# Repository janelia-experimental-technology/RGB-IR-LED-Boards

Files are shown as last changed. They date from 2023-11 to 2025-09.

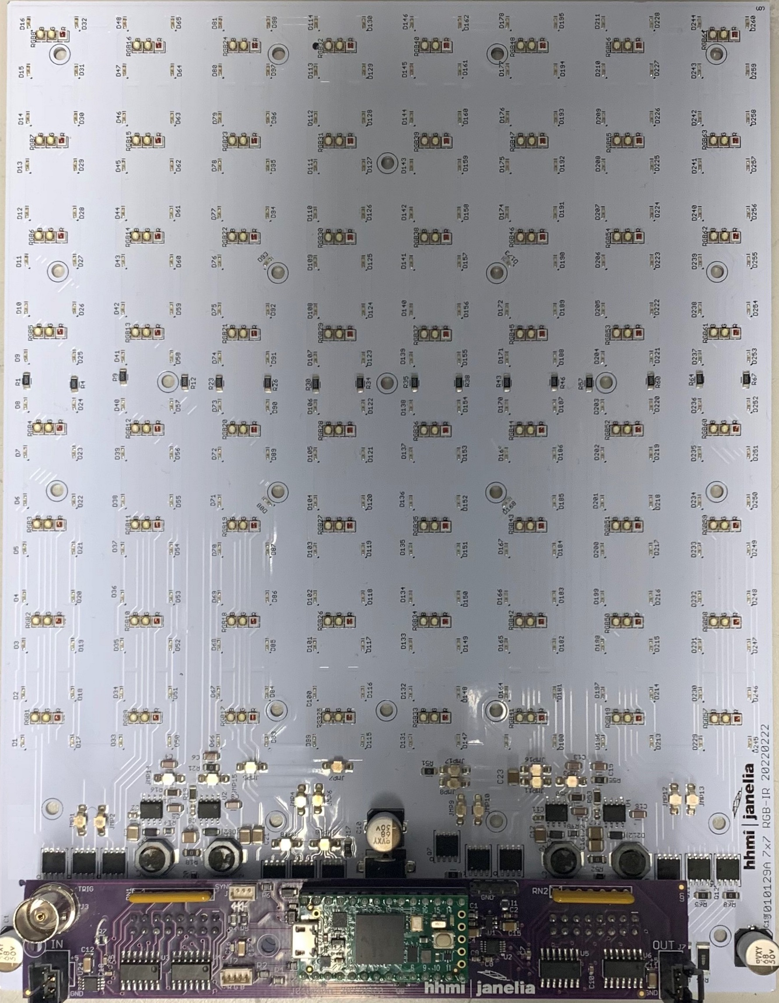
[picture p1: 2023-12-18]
RGB-IR Backlight 7x7/7x7RGB.jpg

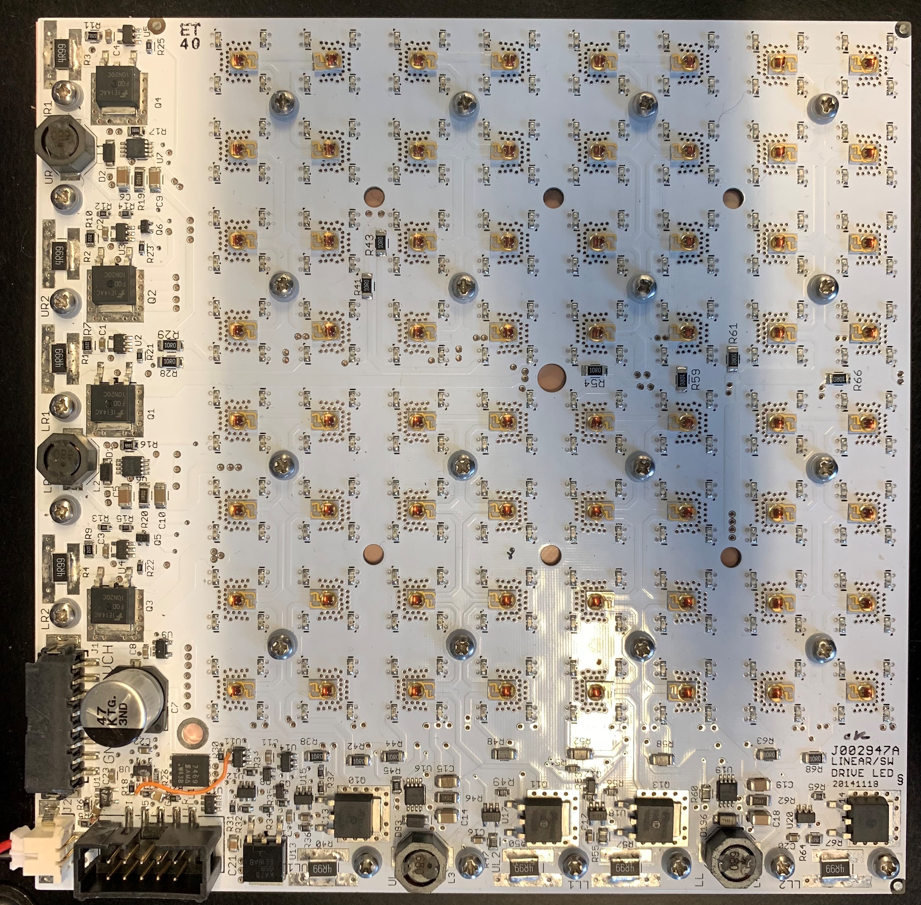
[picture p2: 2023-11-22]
RGB-IR Backlight SingleColor/Electrical/LEDboard-J002947A/J002947A.jpg

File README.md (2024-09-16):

# RGB-IR-LED-Boards
 RGB-IR backlights 
Various LED boards that provide color and IR lighting (primarily for backlighting) in steady or pulsed modes. 
The boards are controlled by a USB-Serial command interface that provides a wide variety of opearting modes.
The 5x5 single color and RGB Combined Color have been depracated and are for reference only. 
The cuurent boards have LED areas of 5" x 5" or 7" x 7" and use separate LEDs for each color, allowing up to
three colors to be used on one board (in addition to IR). The firmware and command interace is common to all 
boards, though some features may not be available on all boards.

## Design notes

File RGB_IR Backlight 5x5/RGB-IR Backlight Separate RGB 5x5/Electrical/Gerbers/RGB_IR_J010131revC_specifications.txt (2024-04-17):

RGB_IR_J010131revC_specifications

2 layers 
0.8mm finished thickness
2 oz copper
white soldermask with black silkscreen

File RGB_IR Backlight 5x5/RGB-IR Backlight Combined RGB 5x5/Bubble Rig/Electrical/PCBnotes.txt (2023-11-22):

The RGB-IR board should be 0.032" thickness with 2 oz copper traces

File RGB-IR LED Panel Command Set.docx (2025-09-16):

RGB-IR LED Panel Command Set

Steve Sawtelle
Lead Electrical Engineer, ID&F
(571) 209-4158

# System Overview

The command set for the RGB-IR LED panels is common to all versions of the 5” x 5” and 7”
x 7” panels designed at Janelia Research Campus of HHMI.

# Firmware Development

The firmware is written in Arduino with Teensyduino extensions. Several libraries are used:

Cmd.h – This has been modified from the version available on Github to add features needed by the firmware. It processes commands sent over USB-Serial and is used to set up parameters and create actions.

Watchdog.h – This is a library written by Peter Polidoro to set up and control a watchdog timer in case the firmware hangs up.

EEPROM.h – This library is used to save setups in non-volatile memory, such as offsets and gains for each quadrant to make the quadrants light intensity more even (especially at low levels).

Several Teensy varieties are supported. The preferred boards are the Teensy 3.2 and 4.0. The LC can be used but has limited memory for Experiment Command Steps. The firmware will compile correctly based on the chosen processor.

The RGB firmware is command driven. The processing of commands is handled by the cmd.h library, which will call the appropriate function once the command line is parsed. These functions end in ‘cmd’. The commands can set up parameters, query settings, or cause action. Commands are ASCII and case insensitive. Parameters are separated by spaces or commas. The command is terminated with a linefeed and carriage return.

Pulse timing or a loaded experiment is based off a millisecond clock, so the basic accuracy of the board is one millisecond. The processing of pulse timing or a loaded experiment is controlled via a four-phase state machine. Each phase runs independently and is associated with one of the three color channels or digital channel. For each phase, an initial state is called, which sets up parameters and timing for the next state. A flag is set to note a change in state and the next state will wait until the last state has completed before it executes its function and sets up the next state.

# There are several compiler defines that affect the operation of the firmware:

# DEBUG – turns on debugging information on USB-serial output.

SYNC_PIN_OUT – if defined, the SYNC pin is set up as output, otherwise it set up as trigger input.

SYNC_ACTIVE_LOW – if defined, the SYNC pin is active low.

# Command Set

The host communications is via a USB-serial link. The Teensy serial driver must be loaded on the host (available from PJRC.com). The link is baud-independent. The communications protocol is based on an ASCII commands with various parameters. Commands are not case sensitive and must be terminated with a carriage return character (‘\r’, 0x0D). Basic error checking is done and ‘cmderr n’ is returned with ‘n’ being a negative integer that can be used to determine the type of error. Commands may return other information to the Host to indicate status. These are still under development.

NOTE: the 7” x 7” RGB panels do not have addressable ‘Quadrants’. For these boards, the ‘Quadrant’ value should be left blank or set to ‘1111’ to select all quadrants.

The following commands are supported:

RESET – reset all boards to their power-on state. This should always be sent at the beginning of a session or after power has been cycled.

RED b p q (or) - control for red (chrimson) LEDs

CHR b p q

BLUE b p q (or) – control for blue LEDs

BLU b p q

GREEN b p q (or) – control for green LEDs

GRN b p q

IR b p q – control for infrared LEDs

Where:

‘b’ is the brightness as a percentage (0-100). A floating-point value can be used.

‘p’ (optional) is the panel to be changed. No value (or 0) will change all panels. 1-4 will select that panel

‘q’ = quadrant(s): 0 = all, or bit pattern (“0011” means turn on quadrants 1 and 2)

These commands control the LED intensity for red, blue, green, or infrared, respectively. For RGB LEDs, very low values (<1%) may show different intensities across the LEDs since they are close to their turn-off state. The RGB LEDs use linear drivers, so the intensity is very linear down to low levels. Note that for RGB LEDs this command only sets intensity, it does not turn the LED on. Use ON and OFF to control LED state. For IR LEDs, the settings should be above 15% due to the way the driver for these LEDs works. To turn off IR, set the intensity to 0%, as IR LEDs do not have separate ON or OFF commands.

Note: If low, equal, intensities are needed, the maximum current can be modified with a hardware change (see Hardware Technical Document for the board), or the offset value for each quadrant can be adjusted by the Offset command.

Note: the current board design uses separate LEDs for each color, enabling one to choose any mix of available colors. If colors other than red, green, or blue are used, then on will need to keep track of which custom color is associated with each channel name.

ON p q – turn on RGB LEDs to their last setting, optional panel(s) and quadrant(s)

OFF p q – turn off RGB LEDs, optional panel(s) and quadrant(s)

When the RGB LEDs are set to an intensity, that value is stored. Use ON and OFF to turn RGB LEDs on and off.

‘p’ = panel(s): 0 = all, or 1, 2, 3, or 4 for an individual panel

‘q’ = quadrant(s): 0 = all, or bit pattern (“0011” means turn on quadrants 1 and 2)

PULSE width, period, number, off, wait, iterations, color - pulse setup command

The PULSE command sets up a pulse train to light Optogenetic LEDs that have been set up with an ON or PATT command. The pulse has: on delay, pulse width, period, number of cycles, off delay, wait time, and number of iterations. WAIT

width: The pulse width (on time) in milliseconds from 1 to 30000

period: The period of the pulse (on time plus off time) in milliseconds from 1 to 30000. If the width and period are equal, then the LEDs are on constantly during the pulse train.

number: The number of pulses in a pulse train. One pulse train starts with an on time and ends ‘number’ of pulse later after the last off time.

off: The off time after the pulse train completes in milliseconds from 0 to 30000. This provides a means to have a dead time between pulse trains if iterations are used. Note that the total off time from when the last pulse on time ends to the next pulse on time starts is equal to: off + period – width.

wait: Delay the start of the pulse sequence in seconds from 0 to 120. This delays the start of the very first pulse after the RUN command is sent. It is not repeated until RUN is resent. A floating-point value can be used here to set timing to the millisecond level.

iterations: The number of time the pulse train is repeated from 0 to 30000. A ‘0’ value runs the pulse train continuously until a STOP command is sent.

color: Which color the pulse command is for (‘R’, ‘G’, and/or ‘B’) – the three characters can be used in any combination. If different pulse setups are required for different colors, then use separate PULSE commands.

The diagram below shows how each parameter fits into the pulse train:

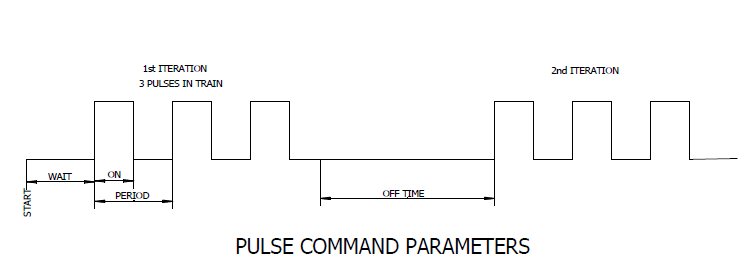
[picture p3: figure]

RUN c- Start running the pulse sequence, optional color(s)

- c – color(s) any combination of ‘R’, ‘G’, ‘B’

STOP c- Stop running the pulse sequence and reset to the beginning, optional color(s)

- c – color(s) any combination of ‘R’, ‘G’, ‘B’

PAUSE – Pause the current pulse sequence

MARKER c s – turn a marker LED on or off.

- c – color: ‘R’, ‘G’, ‘B’, ‘D’
- s – state “ON” or “OFF”

BLINK t c – turn the marker LEDs on for ‘t’ milliseconds. This pattern will also be repeated at the beginning of Each experiment Step.

- c – color(s) any combination of ‘R’, ‘G’, ‘B’

DIGITAL p – set up digital outputs according to bit pattern ‘p’

DON – turn on digital outputs that were enabled with the DIGITAL command

DOFF – turn off digital outputs

SYNC f – send sync pulses out Sync connector at frequency ‘f’ (floating point). If ‘f’ = 0, then turn of sync output. If ‘f’ is blank, return current sync rate.

SYNCON – start sync signal at previously specified rate

??? - Returns the version number and other parameters

HELP - Returns a list of the available commands

EXPERIMENT COMMANDS

A complete experiment can be downloaded to the board, consisting of individual steps that run one after the other. Steps can be loaded in any order, with ‘1’ being the first step. An experiment will stop at the end of the steps (or the first missing step).

addOneStep(parameters): upload one experiment step to the buffer with the following parameters:

StepNumber,

RedIntensity, RedPulsePeriod, RedPulseWidth, RedPulseNum, RedOffTime, RedIteration,

GrnIntensity, GrnPulsePeriod, GrnPulseWidth, GrnPulseNum, GrnOffTime, GrnIteration,

BluIntensity, BluPulsePeriod, BluPulseWidth, BluPulseNum, BluOffTime, BluIteration,

DelayTime, Duration(step), [optional] pattern )

Where:

The Intensity, Period, Width, Number, Off Time, Iteration are the same as the PULSE command

Delay Time is the same as the PULSE command but is common for all three colors

Duration is the total duration of the step

Pattern is the quadrant pattern use (16 bits)

getExperimentsteps (or GS): returns a list of entered steps

removeAllSteps: remove all steps

runExperiment (or RX): run the entered experiment

stopExperiment (or SX) : stop the experiment in progress

getExperimentStatus (or GX): returns the current step being processed during a run

stepOrder n: add a series of numbers, one at a time, designating the sequence the entered Experiment Steps should be run in (if not used, the experiment is run in the step sequence, one time). For example, if 2 steps are entered, sending:

steporder 2

steporder 1

steporder 1

steporder 2

will run step 2, then step 1, then step 1 again, then step 2 when the runExperiment command is sent.

Sending stepOrder 0 will reset the steps, sending stepOrder with no parameter will list the step order.

CALIBRATION COMMANDS

The RGB_IR board should have uniform light output. However, the 5x5 board, with separate quadrant control, may show some differences at low light levels. If an experiment requires background subtraction, then the brightness of each quadrant can be adjusted so that, at a given IR setting, the backlight is more uniform. The light levels can be calibrated using the OFFSET and GAIN commands. These values are stored in non-volatile memory and will be loaded at power up. The offset values represent digital-to-analog converter (DAC) counts. The DAC can range from 0 to 4095. The brightness is calculated as follows:

output value = set value * GAIN + OFFSET

Gain

The GAIN command was added to enter in gain values. These values default to 1.0 and can range from 0.8 and 1.2, but generally, gain changes of 5% or less are enough. A new board has the gains all set to 1.0. There are sixteen gain values: one for each quadrant and for each color. The IR gain is probably the most important as it sets the continuous backlight that is used for automatic tracking. The color LEDs are normally used for optogenetics, and small differences are not as critical.

GAIN c, q, g – set the gain value for a quadrant

Where:

‘c’ is color to be adjusted (‘R’, ‘B’, ‘G’, or ‘I’).

‘q’ = quadrant(s): 0, 1, 2, or 3

‘g’ is the gain multiplier (0.8 to 1.2)

If the GAIN command is sent without parameters, the current settings are returned:

GAIN

BLU 1.00 1.00 1.00 1.00

GRN 1.00 1.00 1.00 1.00

RED 1.00 1.00 1.00 1.00

IR 1.00 1.00 1.00 1.00

To change the gain of a quadrant, the GAIN command has parameters of Color, Quadrant, and Gain:

GAIN BLUE 0 1.1

The color can be spelled out or a shortened version can be used (RED, GRN, BLU, IR) or, simply, just the first letter is needed (R,G,B,I). The commands are case insensitive.

The Quadrant is a value between 0 and 3 inclusive, starting with the quadrant closest to where the cables attach, and increasing clockwise:

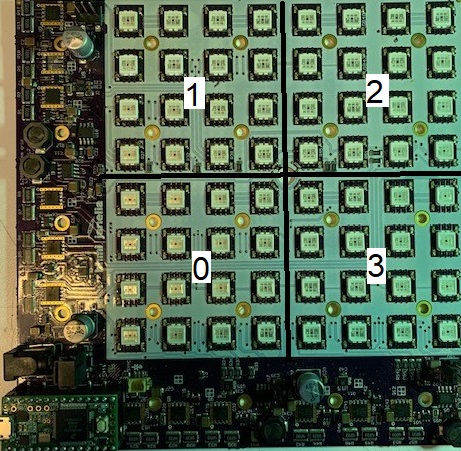
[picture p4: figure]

An example is the Fly Bubble Rig, where the quadrants can be counted relative to the hole at one corner:

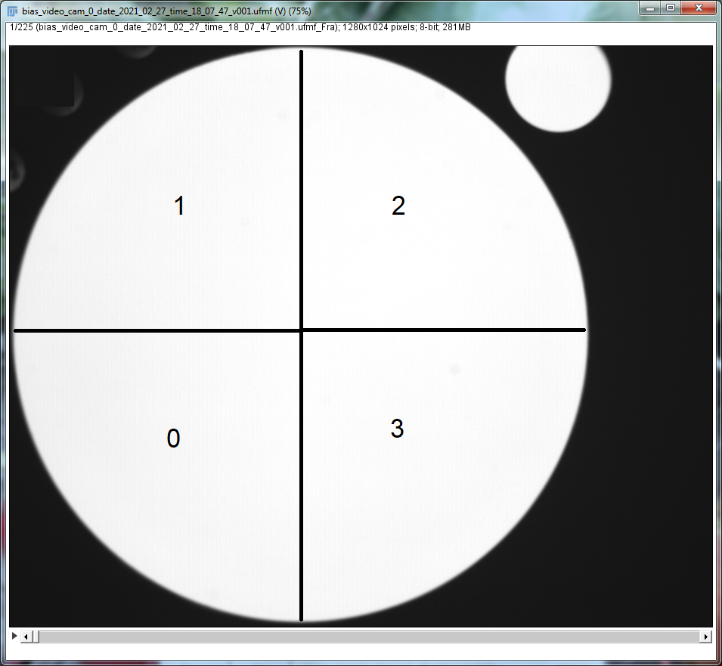
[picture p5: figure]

The Gain is a floating-point value between 0.8 and 1.2 inclusive. Lower gain reduces the relative brightness of the selected quadrant.

An Intensity Command for the chosen color and quadrant must be sent to see the effect of a gain change. So, if IR is changed for quadrant 1, then sending:

IR 30

Will update all the IR’s with appropriate gains.

Choosing the correct gains is somewhat interactive. The easiest method is to set the chosen color to a set intensity for all quadrants slightly below the saturation level, for example:

IR 40

Log a video or single frame of the board using BIAS or other camera software. Open that file in FIJI or other analysis software. Look at profiles of adjacent quadrants:

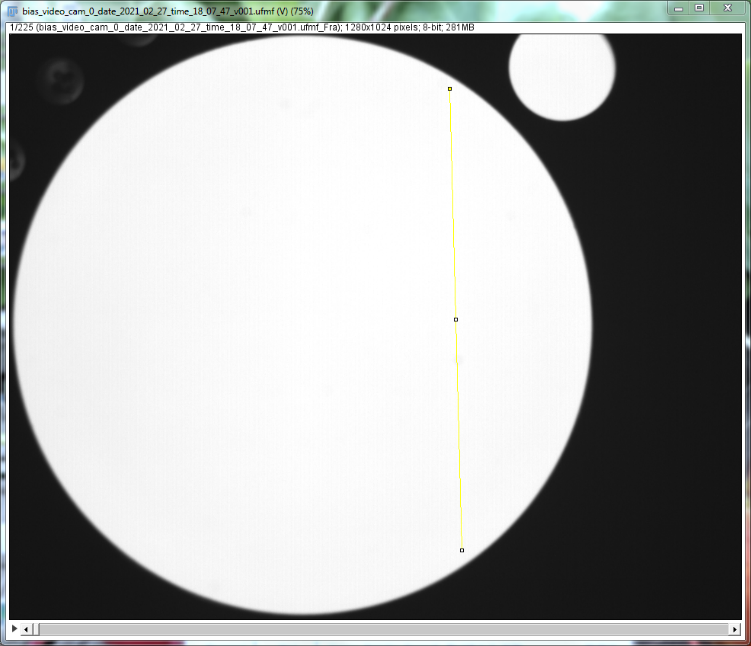
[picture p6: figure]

Here a profile line was drawn through the quadrants 2 and 3. Do this to the other three combinations. It will be clear which quadrants are different than the others. If one quadrant is higher intensity, it’s gain can be lowered, or if one quadrant is lower, it’s gain can be increased. 5% changes are usually enough. Change the IR level to make the gain take effect and repeat until the profiles are sufficiently uniform.

Once the profiles are uniform, the gain changes are complete. The GAIN command, without parameters, can be used to list the changes made. These changes are stored in non-volatile memory, so they are reinstated after a power cycle or reset. However, if the device is reprogrammed with updated firmware, the values may be lost. It would be wise to make note of the values once changes are finalized.

Offset

A zero offset can be applied to each quadrant in a similar way to gain. This is primarily used to get more even brightness at very low settings (less than 2%). Offset values can range between 0 and 20 and is in units of digital-to-analog converter (DAC) counts. The DAC has a range of 0 to 4095 counts.

OFFSET c, q, o – set the offset value for a quadrant.

Where:

‘c’ is color to be adjusted (‘R’, ‘B’, ‘G’, or ‘I’).

‘q’ = quadrant(s): 0, 1, 2 or 3

‘o’ is the offset value (0 to 20)

If no parameters are specified, then the current settings are returned.

# Intraboard Commands

This section describes the commands sent between boards. These commands are not directly available to the host but are included here to provide detail on how host commands are relayed to the other panels. The intraboard communications is based on a TTL serial link using the Teensy Serial1 port. Each panel has an input and output line. All boards have a Teensy installed, but only one (main panel) is connected to the host. The host sends all commands to all or any other panel(s) via the main panel. The main panel interprets the command from the host, and if is destined for one or more other panels, it sends the command on via Serial1. The incoming serial connection to the panel is always connected to the micro’s Serial1 receive port and the outgoing serial connection leaving a panel is routed through a TX/RX switch to route signals. The panel’s output signal can be switched between a direct connection to the input (Parallel Mode) or connected to the panel’s Serial1 transmit port (Series Mode).

Initially, all panels boot up in Parallel Mode. On reset, the main panel will send a Series command to put the attached panels in daisy-chain mode. This is necessary so that the boards can enumerate so they know what position they are in. An initial Enumerate1 command by the main panel propagates to the second panel, which configure itself as panel 2, and it the sends out an Enumerate2 to the second panel. This panel then configures itself as panel 3, and sends an Enumerate3 command to the last panel. After allowing time for the commands to propagate, the main panel sends a Parallel command to set the panels back to normal operation. Then any commands from the main panel are passed directly to all panels simultaneously to minimize delay of commands between panels. Each command is a single 8-bit value. The 256 possible commands are organized as follows:

Commands

00pp bbbb Turn off selected quadrants on selected panels

pp = panel (00 = all, 01 = 1, 10 = 2, 11 = 3)

bbbb = quadrant bits quadrant bits (0b0001 is upper left, 0b0010 upper right, 0b1000 lower right, 0b0100 lower left

01pp bbbb Turn on selected quadrants on selected panels

pp = panel (00 = all, 01 = 1, 10 = 2, 11 = 3)

bbbb = quadrant bits quadrant bits (0b0001 is upper left, 0b0010 upper right, 0b1000 lower right, 0b0100 lower left

10pp qqcc Set intensity command of selected panel(s), quadrants(s) , and color(s) to last Intensity value (0-4095)

pp = panel (00 = all, 01 = 1, 10 = 2, 11 = 3)

qq = quadrant number 00 is upper left, etc.

cc = color (00 = BLU, 01 = RED, 10 = GRN, 11 = IR)

1100 iiii Set the lower 4 bits of the intensity value (or lowest 4 bits of digital pattern)

iiii = intensity value nibble

1101 iiii Set the middle 4 bits of the intensity value (or middle 4 bits of digital pattern)

iiii = intensity value nibble

1110 iiii Set the highest 4 bits of the intensity value (or highest 4 bits of digital pattern)

iiii = intensity value nibble

1111 00xx Enumerate

xx = 01 sent by main board, 10 sent by next panel, 11 sent by third panel

1111 0100 Set RX/TX switch to Series mode

1111 0101 Set RX/TX switch to Parallel mode

1111 1ddd Turn color DACs on or off on all panels (used for fast response, especially for pulsing

ddd = color DACs: bit 2 = red, bit 1 = green, bit 0 = blue

1111 0000 When in parallel mode, turns red marker off

1111 0000 When in parallel mode, turns green marker off

1111 0000 When in parallel mode, turns blue marker off

1111 0111 When in parallel mode, sets digital pin pattern from last pattern sent with Intensity command

1111 0001 When in parallel mode, turn digital outputs on

1111 0011 When in parallel mode, turn digital outputs off

1111 0101 When in parallel mode, turn digital marker off

IR-Optogenetic Panel Controller

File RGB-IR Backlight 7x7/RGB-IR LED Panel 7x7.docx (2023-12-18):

7” x 7” RGB-IR LED Panel

J0010129 and J010130

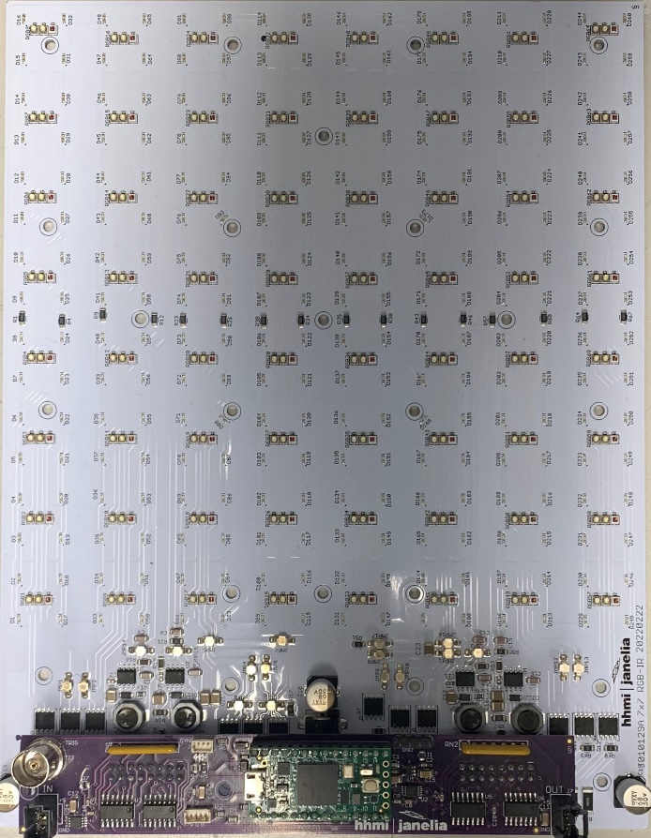
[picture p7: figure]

Steve Sawtelle
Electrical Engineer, ID&F
(571) 209-4000

# System Overview

The RGB-IR LED Panel is used to provide three colors and IR lighting of various intensities. The standard design uses red, green, and blue (RGB) LEDs, but since separate LEDs are used for each color, any three colors can be used that are available in the Luxeon C series palette. A built- in micro-processor controls the panel via a USB-Serial interface. This allows the panel to directly control pulsing of the LEDs, offloading the task from the host computer, and ensuring accurate timing. The panel is divided into four quadrants that can be independently set up with different colors and intensities. The lit area of the panel is 7” x 7” (122mm x 122mm). The overall size of the panel is 6” x 6” (152.6mm x 152.6mm). Four panels can be combined to form a lit area of 9.6” x 9.6” (178 mm x 178 mm). These panels can be daisy-chained so that all panels can have synchronized control through a single USB connection. A three-pin connector can be used to drive an indicator LED and/or perform sync in and out functions. A four-pin connector provides individual marker signals for the RGB light. A five-pin connector provides four digital outputs. The hardware is divided between two printed circuit boards; the LEDs and power circuit are located on an aluminum-backed board to provide optimal heat sinking and the control electronics are located on a plug-in, standard, printed circuit board.

# Hardware Development

The board incorporates a Teensy 4.0 processor with code developed under the Teensyduino environment to make code updates and changes easy. The RGB LEDs are controlled via linear drivers to provide constant levels with no PWM artifacts. The linear control driver is through a standard FET with a low-side current sense resistor driving the feedback control via an op-amp. Since there are two series strings of LEDs in each quadrant, a dual, matched FET is used to passively regulate the second string. Using linear regulators does increase power dissipation, which should be low if the LEDs are pulsed at low duty cycles. The IR LEDs are PWM controlled to lower heat dissipation, as they are typically always on. The IR PWM artifacts are also out of the detection range of most test animals. Multiple panels are controlled by a serial communications link that is daisy-chained from board to board. The RGB LEDs are on 0.6” (15.24mm) grid and the IR LEDs are on a 0.3” (7.62mm) grid.

Schematic - See project file

Printed Circuit Board - See project file

Materials- See project file

# Connectors

J1– (located on LED board) power barrel 2.5 x 5.5 mm

Power In – 28VDC @ 5 Amp minimum

Mini-USB on Teensy

Connects to host computer for control and firmware updates.

J1 – 3 pin latching, Molex 1.25mm connector (533984003), marker and sync I/O

1- Teensy pin 20 through 332 ohms, intended to drive a marker LED.
2- Teensy pin 19 through 100 ohms, intended for a sync input
3- Ground

J2 – 4 pin latching, Molex 1.25mm connector (533984004), marker LEDs connection

These markers are active when the corresponding color LED is active. When a pulse command is being run, the marker ‘envelopes’ the pulse train. These marker LEDs are generally IR LEDs to allow a camera with an IR high pass filter to record when the color LEDs are active.

1- Red marker output through 332 ohms, intended to drive a marker LED.
2- Green marker output through 332 ohms, intended to drive a marker LED.
3- Blue marker output through 332 ohms, intended to drive a marker LED.
4- Ground

J3– BNC, Sync Output

J7 and J8 – 3 pin TE Connectivity 0.1” center (3-647167-3), Board daisy chain

1- ground
2- TX/RX
3- +5VDC

# Setup and Deployment

LED Intensity

Power Supply

A power supply with a rating of 28 volts is required. The current required depends on which LEDs are illuminated and at what maximum intensity. A single color, at 100% intensity, will draw about 2 amps. The IR at 100% intensity will draw about 0.8 amps. Multiple boards can be run from a single power supply, but it must supply the total current needed by all boards. The Cincon TRH100A280-12E13-Level-VI power supply can supply 28V at up to 3.54 volts and can be plugged directly into the RGB board. A single board, with a power requirement of less than 1.2 amps, could use an XP Power ACM36US30, which also can plug directly into the board.

Mounting and heatsinking

The panel needs to be mounted on a minimum 7” x 9” (178 mm x 229 mm) heat sink. The mounting screws (4-40 or 3mm) are on 1” x 1” (25.4 mm x 25.4 mm) grid. This allows the board to mounted on a Thorlabs Imperial dimensioned breadboard. Adapters from the 4-40 (or 3mm) to ¼-20 threads will be needed. A diffuser positioned at least 0.5” (12.7mm) above the panel will provide uniform IR lighting over the lit area. The panel runs off a single 28-volt power supply, although up to 36 volts can be used if duty cycles are low or good heat sinking is employed. At lower duty-cycles the major heat source is the linear regulators (12 large flat ICs), especially the red drivers. If continuous RGB illumination is used then the LEDs become the major heat source. In general, at low illumination and/or duty cycles, a standard breadboard can be used. At higher power levels and longer on times, a liquid cooled breadboard will be needed along with a cooler such as a Koolance EXT-440CU computer cooler.

Panels and Quadrants

The firmware and the 5” x 5” RGB board has four quadrants, each of which can be set to different colors and intensities. The 7” x 7” does not have this feature (though it uses the same firmware).

The 7” x 7” does allow for multiple boards (panels) which can be combined to make a larger illuminated area, either 7” x 28” or 14” x 14”.

The Host USB connection is made to Panel 1 only. Cables are used to daisy-chain Panel 1 to Panel 2, Panel 2 to Panel 3, and Panel 3 to Panel 4. When the RESET command is set, a command is sent along the daisy-chain to enable each panel to understand where it lies in the arrangement. The daisy-chain setup can also be used if to control four separate rigs that only need one panel each. This is especially useful if the four rigs will run the same protocol.

# Command Set

See the separate document: RGB-IR LED Panel Command Set.docx for descriptions of the commands.

# Firmware Description

This section describes, in general terms, how the firmware works.

The firmware is written in Arduino with Teensyduino extensions. Several libraries are used:

Cmd.h – This has been modified from the version available on Github to add features needed by the firmware. It processes commands sent over USB-Serial and is used to set up parameters and create actions.

Watchdog.h – This is a library written by Peter Polidoro to set up and control a watchdog timer in case the firmware hangs up.

EEPROM.h – This library is used to save setups in on-volatile memory, such as offsets and gains for each quadrant to make the quadrants light intensity more even (especially at low levels).

Several Teensy varieties are supported. The preferred boards are the Teensy 3.2 and 4.0. The LC can be used but has limited memory for Experiment Command Steps. The firmware will compile correctly based on the chosen processor.

The RGB firmware is command driven. The processing of commands is handled by the cmd.h library, which will call the appropriate function once the command line is parsed. These functions end in ‘cmd’. The commands can set up parameters, query settings, or cause action. Commands are ASCII and case insensitive. Parameters are separated by spaces or commas. Each command is terminated with a linefeed and carriage return.

The timed functions of the board are based on a one millisecond timer, so the basic accuracy of the board is one millisecond. The processing of timing functions is controlled via a four-phase state machine, one phase for each color and a fourth for digital outputs. An initial state is called, which sets up parameters and timing for the next state. A flag is set to note a change in state and the next state will wait until the last state has completed before it executes its function and sets up the next state.

There are two main timed functions: Pulse and Experiment:

The Pulse function is used to create a train of pulses at a set rate. See the PULSE command for details. Each color (and digital output) can have its own pulse setup and they can run concurrently.

The Experiment function can be used to create an entire experiment setup consisting of various pulse setups that can be varied over an experimental run. This is especially useful in complex experiments as all the timing can be offloaded to the RGB Board from the host.

IR-Optogenetic Panel Controller

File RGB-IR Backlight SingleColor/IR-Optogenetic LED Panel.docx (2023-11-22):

IR-Optogenetic LED Panel

Vault Folder: Fly Bowl LEDs

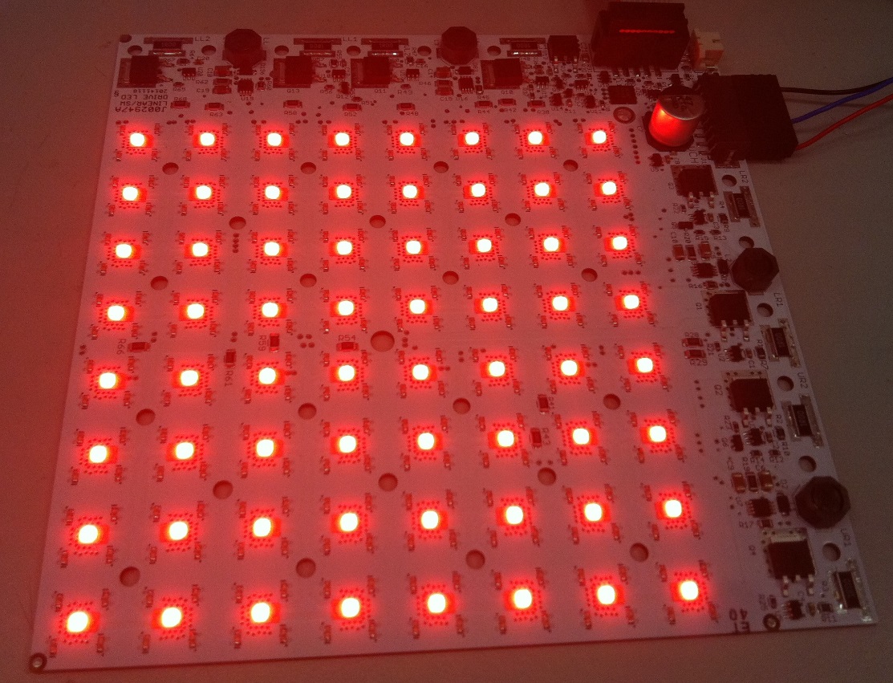
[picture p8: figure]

Steve Sawtelle
Lead Electrical Engineer, ID&F
(571) 209-4158

# System Overview

The IR-Optogenetic LED Panel provides IR (infrared) backlight and optogenetic illumination. The typical application is backlighting for larva or flies, though it can used in other types of experimental setups. The illuminated area is about 114 x 114 mm (4.5 x 4.5 inches). The optogenetic lighting is broken up into four quadrants to allow targeted optogenetic activation. Four panels can be set up in a square to provide a 228 mm x 228 mm (9 x 9 inches) backlight, resulting in 16 areas with independent on/off control.

The IR lighting (850nm) is controlled by a single 0-2.5V analog signal (voltage below 0.2V is off). The optogenetic lighting has a single intensity control provided by a 0-2.5V analog signal. Four on/off controls provide the means to turn each optogenetic lighting quadrant on and off. The control signals can be manual (a 5V source is provided to drive external potentiometer/voltage dividers and switches), via a NI-DAQ (or similar digital/analog I/O board), or via the HHMI/Janelia IR/Optogenetic Panel Controller.

A marker signal is available and is typically used to light a separate IR LED in sync with any optogenetic on/off control being on. This allows a camera with a high pass filter to record when optogenetic stimulation is occurring. The marker signal is a logic OR of the 4 on/off signals and the marker input signal. If the marker signal is on when one of the on/off signals is active, the marker LED intensity will increase, which may be useful in certain protocols.

The board should be mounted on a heat sink using 3mm or #4 screws. Plastic washers or screws must be used to prevent shorting tracks on the top of the printed circuit board. A non-electrically conductive thermal pad (such as t-Global H48-6G-300-300-0.3) should be used between the board and the heat sink. The heat sink requirements vary depending on the LED intensities used and the duty cycle. For low light, a piece of aluminum plate may be sufficient, higher intensities may require a finned heat sink or cold plate. Adapter plates can be made to attach the panel to a standard optical breadboard or cold plate.

A 6.3mm (1/4”) hole is placed in the center of the lighted area to allow for plumbing or wiring to extend up through the board.

A minimum component-free space of 2.5mm (0.1”) is provided between quadrants to allow for vertical light barriers to be added to the top of the panel.

A diffuser is required to create uniform lighting. A diffuser can be made from 3mm (1/8”) white acrylic placed 12mm (1/2”) or more above the panel.

Power for the board is supplied by two separate supplies (one for IR and the other for optogenetic and control). The default setup, at maximum intensity, requires an IR supply of 36VDC at 0.8A, and an optogenetic supply of 24VDC at 3.2A.

Hardware Development

Different optogenetic experiments require different light intensities to achieve proper activation. This depends on the subject (fly/larva), targeted area, and activation type. The board was designed to maximize the flexibility in setting intensity, while minimizing heating. Although PWM (pulse width modulation) is the highest efficiency control, it is limited in range and may be problematic if the experiment’s on/off control is pulsed at a high rate. Since the optogenetic lighting is usually intermittent, it was decided to use linear intensity control to provide the broadest range in intensity and remove any question of PWM effects on the experiment. On the other hand, the IR lighting is usually on full time and does not require as fine adjustment, so a PWM driver is used here. This is also out of the visible wavelength range for a fly.

Current sense resistors are used in both lighting controls to set maximum intensity. These can be changed to provide lower ranges (useful in larva experiments). The optogenetic lighting uses a constant current source with a sense resistor between the power FET source and ground. The maximum current is set by Imax = 0.4V/R. The board is designed with a 1 ohm sense resistor, which yields 0-400mA of current control. Higher value resistors can be used to change the range, i.e.: a 5 ohm resistor would allow a maximum of 80 mA. A lower value resistor could be used to get higher current, but most of the Rebel Luxeon LEDs (used on this board for optogenetic light) are limited to 350mA. The resistor is a size 2512 (reversed 1225). There are eight of these per board and their locations are obvious as they are the only large resistors on the board. The IR intensity control uses a PWM driver. The sense resistor for this circuit provides maximum current control equal to 0.2V/R. This current is shared between 4 strings of IR LEDs, so each LED current is equal to 0.05V/R. The default resistor is 1 ohm so maximum current per LED is 50mA. The IR LEDs handle up to 100mA, so a sense resistor as low as 0.5 ohms could be used, though the default setting works well for most camera setups. These sense resistors are size 1206 and there are four per board located just at the end of each driver chip (AP8802 in an SO-8 package).

Using two power supplies allows the use of inexpensive wall power supplies, and reduces heating by matching the supply to the loads. It also reduces crosstalk between the lighting, so that IR intensity is not very affected by possible high current pulsing of the optogenetic lighting.

Schematic, Printed Circuit Board, Materials

See addendum – IR/Optogenetic LED Panel.pdf

# Connectors

J1 2.1mm x 5.5m DC Power Barrel jack

Power input for optogenetic. 24V at 3.2A.

J1 2.5mm x 5.5m DC Power Barrel jack

Power input for IR. 36V at 0.8.

J3 – 2 pin, 2mm header (Hirose DF3DZ-2P-2H(51)); Mates with Receptacle DF3-2S-2C and terminals DF3-2428SCFC. Pre-terminated wires available from Digi-Key.

Connection for external marker LED. Pin 1 attaches to the LED cathode, pin2 to the anode.

JP1– 2x5 ribbon cable header

This header is used for control signal for the panel:

Pinout

Pin | Function
1 | Optogenetic lower left on/off (TTL high is on)
2 | Optogenetic upper left on/off (TTL high is on)
3 | Optogenetic lower right on/off (TTL high is on)
4 | Optogenetic upper right left on/off (TTL high is on)
5 | Ground
6 | Marker signal (low turns on marker)
7 | +5V out (low current)
8 | Optogenetic brightness control (0-2.5V in analog)
9 | IR brightness control (0-2.5V in analog)
10 | Ground

# Control

The panel can be controlled manually, via an I/O board (such as a NI-DAQ), or a dedicated controller (Janelia IR/Optogenetic Panel Controller).

Manual Operation

The on board 5V output can be used to make a manual controller:

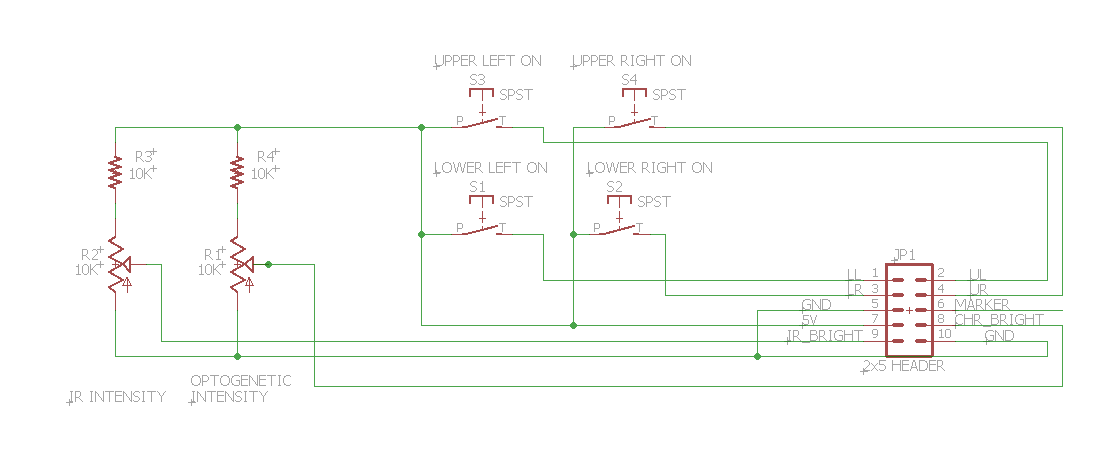
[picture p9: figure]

I/O Board Control

An I/O Board such as a NI-DAQ can be used to control the panel. A panel requires two 0-2.5V analog voltages to set intensity and 4 TTL compatible signals for optogenetic on/off control. The TTL signals are active high and must be able to source 5mA of current.

Dedicated Controller

The HHMI/Janelia IR/Optogenetic Panel Controller is designed to directly control up to four panels. A host computer can communicate with it via a USB/Serial connection. See the documentation for this device for details.

Confidential IR-Optogenetic LED Panel

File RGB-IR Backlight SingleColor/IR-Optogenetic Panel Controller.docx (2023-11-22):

IR-Optogenetic LED Panel Controller

Vault Folder: Fly Bowl LEDs

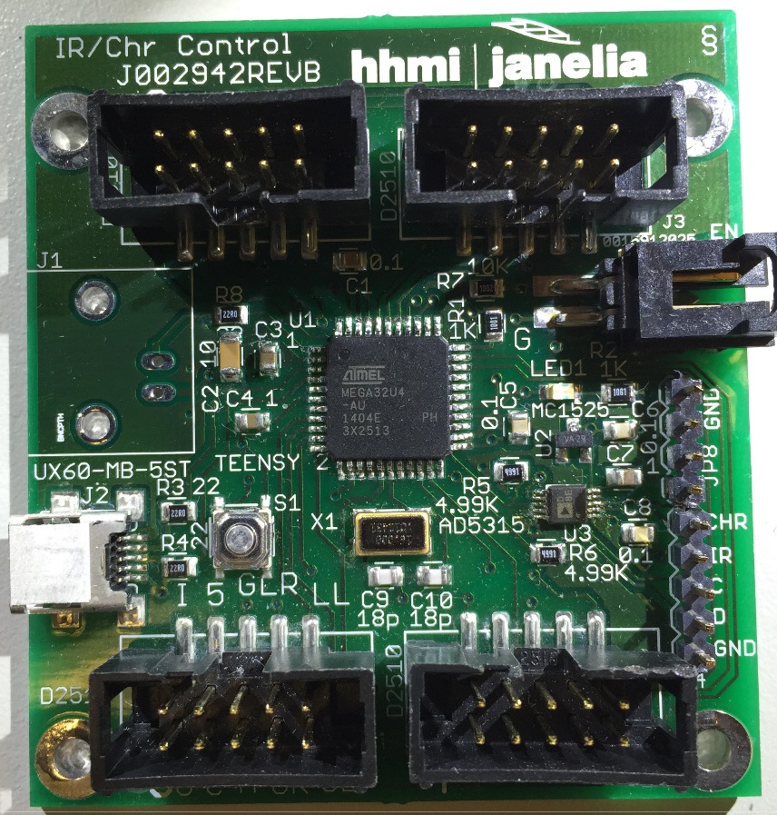
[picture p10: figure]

Steve Sawtelle
Lead Electrical Engineer, ID&F
(571) 209-4158

# System Overview

The IR-Optogenetic Panel Controller is used to control light intensity, pulsing, and pattern generation for up to four LED IR (Infrared) backlight/optogenetic panels. The controller utilizes USB-serial communications to the host to receive commands and return status. A pulse pattern can be downloaded and run by the controller with timing independent from the host to allow precise pulse generation.

# Hardware Development

The board incorporates a Teensy 2.0 processor to make code updates and changes easy. Four ten-pin ribbon cable connectors are used to connect to up to four LED panels. The IR intensity and optogenetic intensity (0-100%) can be set independently, but are each common to all boards. IR on/off control is accomplished by setting the IR intensity to zero. The optogenetic LEDs are arranged in four quadrants on each panel, with independent on/off control. In this way, up to sixteen different areas of light activation can be turned on and off independently. Each panel connector also has a Marker LED that can be used to drive an IR LED off to the side of the arena so that optogenetic LED status can be monitored by an optogenetic-blocking camera. The board has four mounting holes on 2” centers which facilitates attaching the board to a standard one-inch-center optical breadboard.

Schematic

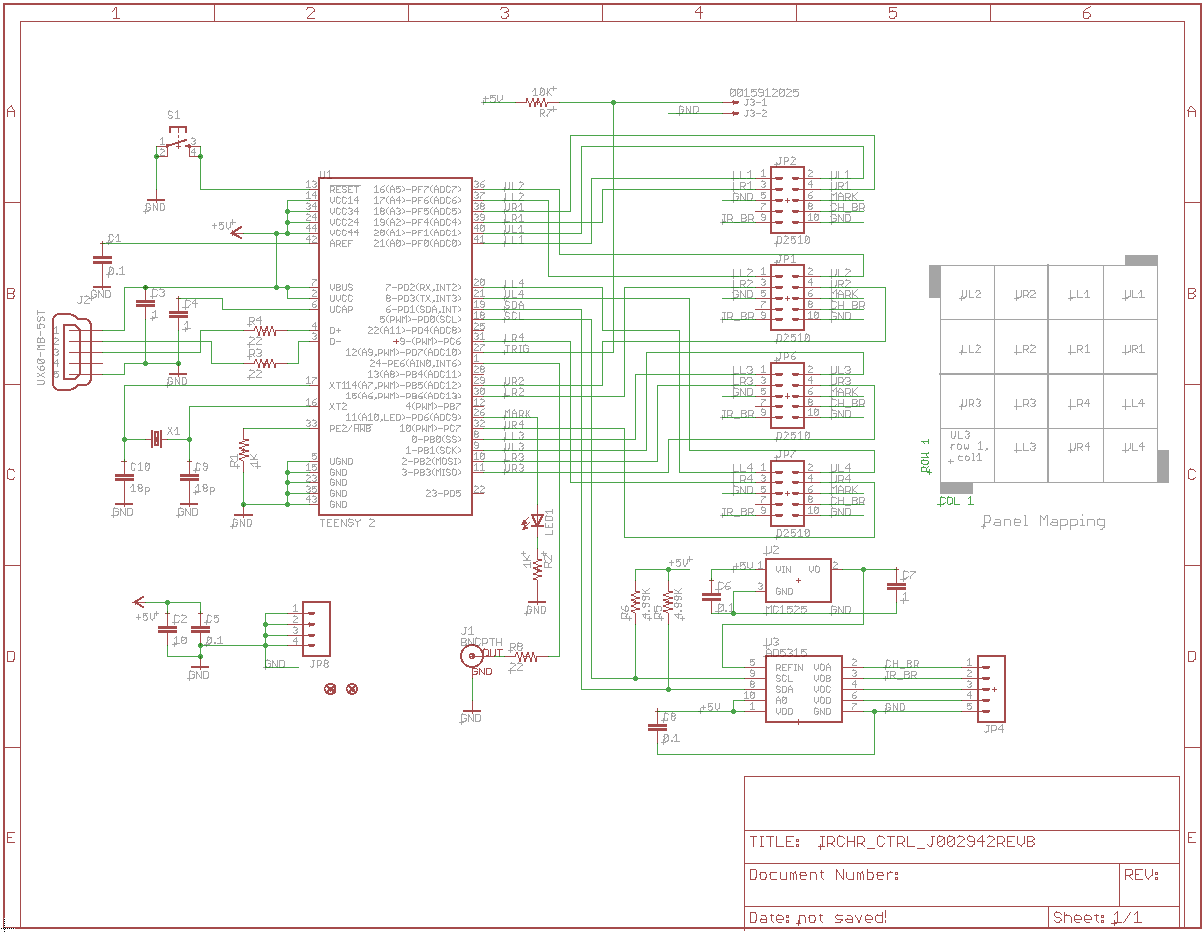
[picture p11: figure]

Printed Circuit Board

See project file

Materials

See project file

# Connectors

J1 BNC

Available for custom use as input or output.

J2 Mini-USB

Connects to host computer for control and firmware updates

J3 – 2 pin latching header (TE Connectivity 103635-1; Mates with Receptacle 104257-1 and terminals 1-104480-5)

Connection for either trigger in or sync out.

JP1, JP2, JP6, JP7 – 2x5 ribbon cable header

These headers connect up to four panels to the controller.

Pinout

Pin | Function
1 | Optogenetic lower left on/off
2 | Optogenetic upper left on/off
3 | Optogenetic lower right on/off
4 | Optogenetic upper right left on/off
5 | Ground
6 | Maker LED out
7 | +5V from panel (not used on this board)
8 | Optogenetic brightness control (0-2.5V out analog)
9 | IR brightness control (0-2.5V out analog)
10 | Ground

# Firmware Development

The firmware is written under the Arduino programming environment with Teensy extensions added in. There are three compiler defines that affect the operation of the firmware:

USE_SCALING - normally undefined

If undefined, the brightness of the optogenetic LED is set in a linear fashion. If defined the brightness is set with pseudo-log scaling, such that up to 40%, the LED brightness increases in a small step linear fashion, and above 40%, it increases logarithmically.

LINEAR_DRIVER – normally defined

This should be defined when used with the current panel design. Earlier panels used a PWM brightness control for the optogenetic LEDs and required an offset in the brightness setting.

USE_EXT_TRIG - normally undefined

If defined, an external trigger can be used to turn the optogenetic LEDs on and off.

# Command Set

The host communications is via a USB-serial link. The Teensy serial driver must be loaded on the host (available from PJRC.com). The link is baud-independent. The communications protocol is based on an ASCII commands with various parameters. Commands are case insensitive and must be terminated with a carriage return character (‘\r’, 0x0D). Basic error checking is done and ‘cmderr n’ is returned with ‘n’ being a negative integer that can be used to determine the type of error. Commands may return other information to the Host to indicate status. These are still under development.

The following commands are supported:

CHR p – set optogenetic level to ‘p’ percent of full brightness

This does not turn LEDS on. If set to 0% LEDs will turn off, but it is recommended to use the TTL controls for that (via OFF or PULSE command). Very low levels (1 or 2%) may have more variability in individual LED brightness. NOTE: The command was named after ‘CHRimson’ optogenetic lighting as this was the original use. However, the panels can be assembled with a variety of LED colors, so the generic term ‘optogenetic’ is used in this document.

IR p – set IR level to ‘p’ percent of full brightness.

A setting below about 10% will turn off the IR LEDs. There is no separate TTL control. Values near 10% may have inconstant individual LED brightness. It is best to set brightness to 0% if the LEDs should be off. Use values above 10% to turn on the LEDs to a percent of full brightness.

ON x, y – turn on quadrant of optogenetic LEDs at position x and y

Each LED board is divided into four quadrants of optogenetic LED control. Up to four boards can be controlled, so there are sixteen quadrants total in a 4x4 arrangement. The board numbers are 1-4 in a rectangular coordinate system fashion (Quadrant 1 is to the upper right, 2 is upper left, 3 lower left, 4 lower right). If the boards are connected to the appropriate numbered connectors on the controller (also set up in the same order), then one easily select an LED (or groups of LEDs) to turn on. The control is row and column, with row 1 being the lowest and column 1 being the left most. So 1,1 references the lower left quadrant of board 3. Entire rows and columns can be changed at one time by setting the value to 0; so ON 1,0 turn on row 1, all columns. Setting ON 0,0 turns on all crimson LEDS, and is the general way the command is used when no patterns are needed.

OFF x,y – turn off quadrant of Optogenetic LEDs at position x,y

Turns off one or more quadrants of LEDs based on x and y; see the ON command for details.

PATT bbbbbbbbbbbbbbbb – download a Optogenetic ‘on’ pattern

The Pattern command allows an arbitrary pattern of LEDs to be set based on the 16 binary values ‘b’. ’0’ is off. This command does not turn on or off any LEDs directly. The pattern is used in the PUSLE command.

The bits control LEDs in the following pattern (row, column):

If the leftmost bit in the pattern is called ‘b15’ down to ‘b0’ for the rightmost bit:

b3 | b2 | b1 | b0
b7 | b6 | b5 | b4
b11 | b10 | b9 | b8
b15 | b14 | b13 | b12

PULSE width, period, number, off, wait, iterations - pulse setup command

The PULSE command sets up a pulse train to light Optogenetic LEDs that have been set up with an ON or PATT command. The pulse has on delay, pulse width, period, number of cycles, off delay, and number of iterations:

width: The pulse width (on time) in milliseconds from 1 to 30000

period: The period of the pulse (on time plus off time) in milliseconds from 1 to 30000. If the width and period are equal, then the LEDs are on constantly during the pulse train.

number: The number of pulses in a pulse train. One pulse train starts with an on time and ends ‘number’ of pulse later after the last off time.

off: The off time after the pulse train completes in milliseconds from 0 to 30000. This provides a means to have a ‘dead time‘ between pulse trains if iterations are used. Note that the total off time from when the last pulse on time ends to the next pulse on time starts is equal to: off + period – width.

wait: Delay the start of the pulse sequence in milliseconds from 0 to 120. This delays the start of the very first pulse after the RUN command is sent. It is not repeated again until RUN is resent.

iteratations: The number of time the pulse train is repeated from 0 to 30000. A ‘0’ value runs the pulse train continuously until a STOP command is sent.

RUN - Start running the pulse sequence

STOP - Stop running the pulse sequence and reset to the beginning

??? - Returns the version number and other parameters

Confidential IR-Optogenetic Panel Controller

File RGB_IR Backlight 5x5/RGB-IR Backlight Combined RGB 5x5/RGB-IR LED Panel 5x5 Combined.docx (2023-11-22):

5” x 5” RGB-IR LED Panel

J00717 Version REV A

NOTE: This document describes a board design has been deprecated. The 5”x 5” Board with separate RGB LEDs should be used instead.

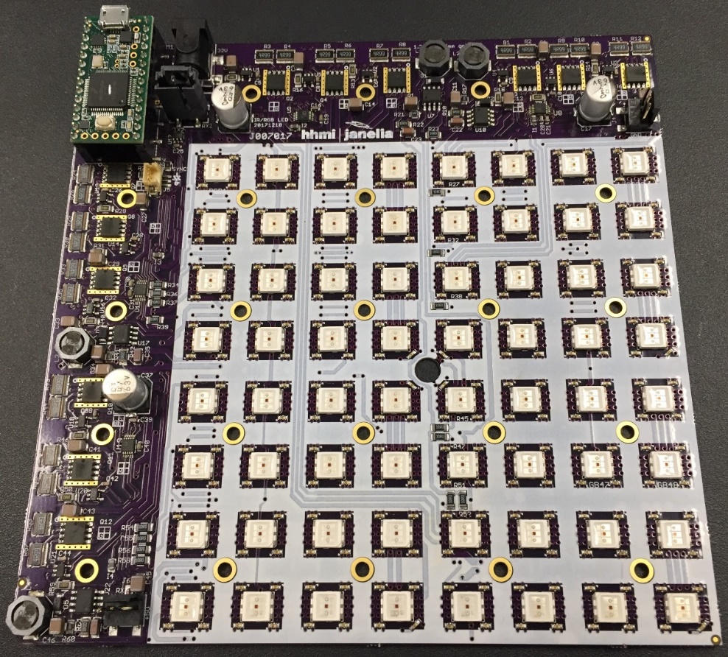
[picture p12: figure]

Steve Sawtelle
Lead Electrical Engineer, ID&F
(571) 209-4158

# System Overview

The RGB-IR LED Panel is used to provide red, green, blue, and/or IR lights of various intensities. A built- in micro-processor controls the panel via a USB-Serial interface. This allows the panel to directly control pulsing of the LEDs, offloading the task from the host computer, and ensuring accurate timing. The panel is divided into four quadrants that can be independently set up with different colors and intensities. The lit area of the panel is 4.8” x 4.8” (122mm x 122mm). The overall size of the panel is 6” x 6” (152.6mm x 152.6mm). Four panels can be combined to form a lit area of 9.6” x 9.6” (244mmx 244mm). These panels can be daisy-chained so that all panels can have synchronized control through a single USB connection. A three-pin connector can be used to drive an indicator LED and/or perform sync in and out functions. A four-pin connector provides individual marker signals for the RGB light. An add-on board can be used to provide digital outputs.

# Hardware Development

The board incorporates a Teensy 3.2 processor with code developed under the Teensyduino environment to make code updates and changes easy. The RGB LEDs are controlled via linear drivers to provide constant levels with no PWM artifacts. The linear control driver is through a standard FET with a low-side current sense resistor driving the feedback control via an op-amp. Since there are two series strings of LEDs in each quadrant, a dual, matched FET is used to passively regulate the second string. Using linear regulators does increase power dissipation, which should be low if the LEDs are pulsed at low duty cycles. The IR LEDs are PWM controlled to lower heat dissipation, as they are typically always on. The IR PWM artifacts are also out of the detection range of most test animals. Multiple panels are controlled by a serial communications link that is daisy-chained from board to board. The RGB LEDs are on 0.6” (15.24mm) grid and the IR LEDs are on a 0.3” (7.62mm) grid.

Schematic

See project file

Printed Circuit Board

See project file

Materials

See project file

# Connectors

J1 – power barrel 2.5 x 5.5 mm

Power In – 28VDC @ 5 Amp minimum

Mini-USB on Teensy-3.2

Connects to host computer for control and firmware updates

J5 – 3 pin latching, Hirose DF13 series, marker and sync I/O

1- Teensy pin 20 through 332 ohms, intended to drive a marker LED.
2- Teensy pin 19 through 100 ohms, intended for a sync input
3- Ground

J5 – 4 pin latching, Hirose DF13 series, marker LEDs connection

These markers are active when the corresponding color LED is active. When a pulse command is being run, the marker ‘envelopes’ the pulse train. These marker LEDs are generally IR LEDs to allow a camera with an IR high pass filter to record when the color LEDs are active.

1- Red marker output through 332 ohms, intended to drive a marker LED.
2- Green marker output through 332 ohms, intended to drive a marker LED.
3- Blue marker output through 332 ohms, intended to drive a marker LED.
4- Ground

J2-J3 – 3 pin connector; 0.1 center

Board daisy chain

1- ground
2- TX/RX
3- +5VDC

# Setup and Deployment

LED Intensity

Power Supply

A power supply with a rating of 28 volts is required. The current required depends on which LEDs are illuminated and at what maximum intensity. Multiple boards can be run from a single power supply but it must supply the total current needed by all boards. The Cincon TRH100A280-12E13-Level-VI power supply can supply 28V at up to 3.54 volts and can be plugged directly into the RGB board. A single board, with a power requirement of less than 1.2 amps, could use an XP Power ACM36US30, which also can plug directly into the board.

Mounting and heatsinking

The panel needs to be mounted on a 6” x 6” (152.4mm x 152.4mm) non-conductive heat sink using a 5x5 array of 4-40 (or 3mm) tapped holes on 1.2” (30.48mm) centers. A diffuser positioned at least 0.5” (12.7mm) above the panel will provide uniform IR lighting over the lit area. The panel runs off a single 28-volt power supply, although up to 36 volts can be used if duty cycles are low or good heat sinking is employed. At lower duty-cycles the major heat source is the linear regulators (12 large flat ICs), especially the red drivers. If continuous RGB illumination is used then the LEDs become the major heat source. In general, at low illumination and/or duty cycles, a flat plate at least ¼” (6mm) can be used. Alternatively, a finned heat sink such as Aavid 601403B06000 can be used. At higher power levels and longer on times, liquid cooling will be needed using a cold plate such as Aavid 416101U00000G and a cooler such as a Koolance EXT-440CU computer cooler. A non-conductive thermal pad is recommended between the board and the heatsink, such as Berqquist GPHC5.0-0.020-02-0816.

Panels and Quadrants

Each RGB board (panel) has four quadrants, each of which can be set to different colors and intensities.

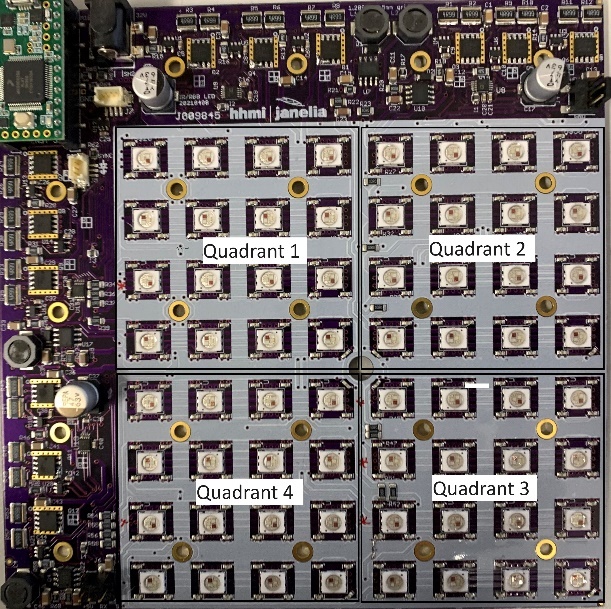
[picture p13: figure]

The quadrants are specified in commands with a four-bit binary value, so for example, if only quadrant 1 should be on, specify ‘0001’. For quadrants 2 and 4, specify ‘1010’. If the quadrant value is not specified in a command, it is assumed all quadrants should be on.

Four panels can be combined to make a larger illuminated area:

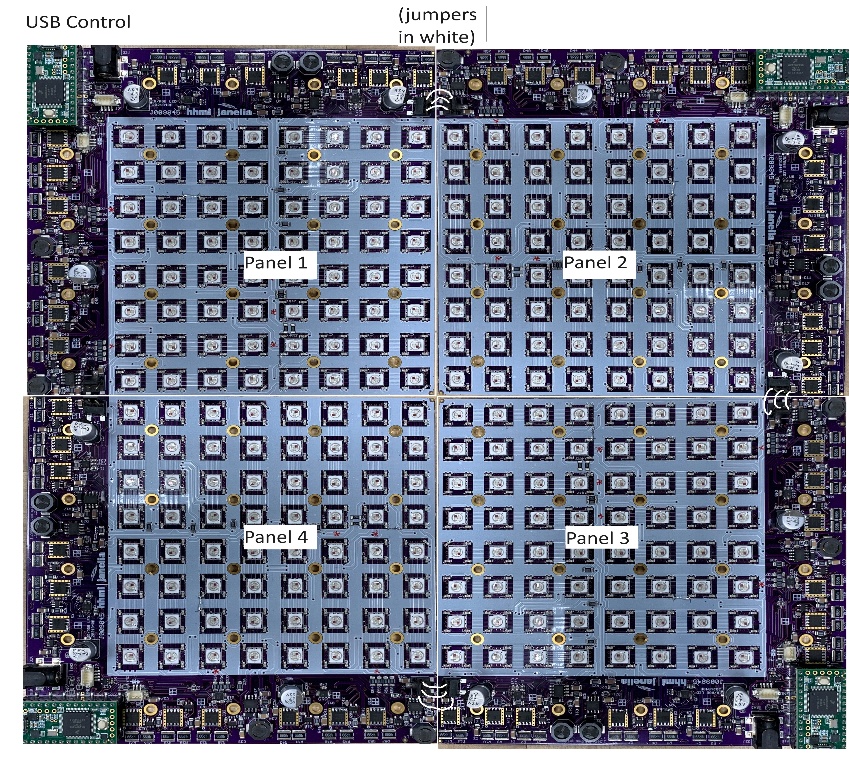
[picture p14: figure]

The Host USB connection is made to Panel 1 only. Cables are used to daisy-chain Panel 1 to Panel 2, Panel 2 to Panel 3, and Panel 3 to Panel 4. When the RESET command is set, a command is sent along the daisy-chain to enable each panel to understand where it lies in the arrangement. When sending commands to specific panels, they are specified in a similar fashion to the quadrants as described above. Note, that, since each panel is rotated differently from the others, then the quadrants are also rotated. It is necessary to map the quadrants correctly when lighting a particular quadrant on a particular panel. The daisy-chain setup can also be used if to control four separate rigs that only need one panel each. This is especially useful if the four rigs will run the same protocol.

# Command Set

See the separate document: RGB-IR LED Panel Command Set.docx for descriptions of the commands.

# Firmware Description

This section describes, in general terms, how the firmware works.

The firmware is written in Arduino with Teensyduino extensions. Several libraries are used:

Cmd.h – This has been modified from the version available on Github to add features needed by the firmware. It processes commands sent over USB-Serial and is used to set up parameters and create actions.

Watchdog.h – This is a library written by Peter Polidoro to set up and control a watchdog timer in case the firmware hangs up.

EEPROM.h – This library is used to save setups in on-volatile memory, such as offsets and gains for each quadrant to make the quadrants light intensity more even (especially at low levels).

Several Teensy varieties are supported. The preferred boards are the Teensy 3.2 and 4.0. The LC can be used but has limited memory for Experiment Command Steps. The firmware will compile correctly based on the chosen processor.

The RGB firmware is command driven. The processing of commands is handled by the cmd.h library, which will call the appropriate function once the command line is parsed. These functions end in ‘cmd’. The commands can set up parameters, query settings, or cause action. Commands are ASCII and case insensitive. Parameters are separated by spaces or commas. Each command is terminated with a linefeed and carriage return.

The timed functions of the board are based on a one millisecond timer, so the basic accuracy of the board is one millisecond. The processing of timing functions is controlled via a four-phase state machine, one phase for each color and a fourth for digital outputs. An initial state is called, which sets up parameters and timing for the next state. A flag is set to note a change in state and the next state will wait until the last state has completed before it executes its function and sets up the next state.

There are two main timed functions: Pulse and Experiment:

The Pulse function is used to create a train of pulses at a set rate. See the PULSE command for details. Each color (and digital output) can have its own pulse setup and they can run concurrently.

The Experiment function can be used to create an entire experiment setup consisting of various pulse setups that can be varied over an experimental run. This is especially useful in complex experiments as all the timing can be offloaded to the RGB Board from the host.

IR-Optogenetic Panel Controller

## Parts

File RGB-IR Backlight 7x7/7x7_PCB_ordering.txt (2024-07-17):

The boards are available on CircuitHub:

https://circuithub.com/projects/sawtelles/7x7LEDcontroller/revisions/56201/parts

https://circuithub.com/projects/sawtelles/7x7_RGB-IR_Backlight/revisions/56283/parts

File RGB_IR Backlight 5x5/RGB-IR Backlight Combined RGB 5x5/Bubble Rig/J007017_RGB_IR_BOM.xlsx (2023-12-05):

J007017_RGB_IR
Qty | Value | Device | Designators | Manufacturer | Man PN | Vendor | Vendor PN | $ea | $Total | Notes
3 |  | 47µF 63V Aluminum Capacitors Radial, Can - SMD 2000 Hrs @ 85°C | C17 C18 C37 | Nichicon | UUR1J470MNL1GS | DK | 493-6235-1-ND | $0.52 | $1.56
1 | 3pos header | CONN HEADER 3POS 1.25MM SMD GOLD | J5 | Hirose | DF13C-3P-1.25V(50) | DK | H3433-ND | $0.73 | $0.73
256 | IR LED | Infrared (IR) Emitter 860nm 1.5V 100mA 9mW/sr @ 100mA 140° 2-SMD, Flat Lead | IR1-IR256 | OSRAM | SFH 4050-Z | DK | 475-2864-1-ND | $0.48 | $122.62
1 | jack | POWER_JACK_SHUNTPJ-002 | J2 | CUI | PJ-002BH-SMT-TR | DK | CP-002BHPJCT-ND | $1.89 | $1.89
2 | header | CONN RCPT .100" 14POS SNGL VERT | M1 | Samtec | SSM-114-L-SV | DK | SAM1148-14-ND | $4.42 | $8.84 | socket for M1
1 | CPU | TEENSY 3.2 + HEADER | M1 | Adafruit | 2756 | DK | 1528-2385-ND | $24.94 | $24.94
22 | 0.1 | CAP CER 0.1UF 50V X7R 0603 | C5 C6 C7 C8 C9 C10 C16 C19 C20 C21 C24 C25 C26 C28 C30 C31 C32 C38 C39 C40 C42 C44 | Kemet | C0603C104K5RACTU | DK | 399-5089-1-ND | $0.03 | $0.62
4 | 1R00 | RES SMD 1 OHM 1% 1/4W 1206 | R20 R22 R42 R61 | Vishay | RCA12061R00FKEA | DK | 541-2240-1-ND | $0.13 | $0.52
4 | 2.2@50 | CAP CER 2.2UF 100V X7S 1206 | C22 C23 C35 C47 | TDK | C3216X7S2A225K160AB | DK | 445-5207-1-ND | $0.57 | $2.28
4 | 4.99K | RES SMD 4.99K OHM 1% 1/2W 0805 | R17 R21 R41 R60 | Vishay | CRCW08054K99FKEAHP | DK | 541-4.99KTCT-ND | $0.24 | $0.96
1 | 100 | RES SMD 100 OHM 1% 1/2W 0805 | R62 | Vishay | CRCW0805100RJNEA | DK | 541-100ACT-ND | $0.10 | $0.10
1 | 332 | RES SMD 332 OHM 1% 1/8W 0805 | R25 | Vishay | CRCW0805332RFKEA | DK | 541-332CCT-ND | $0.10 | $0.10
24 | 4R99 | RES SMD 4.99 OHM 1W 1812 WIDE | R1 R2 R3 R4 R5 R6 R7 R8 R9 R10 R11 R12 R24 R26 R29 R30 R33 R35 R43 R44 R48 R49 R53 R57 | Vishay | RCL12184R99FKEK | DK | 541-2430-1-ND |  | $0.00
16 | 10@50 | CAP CER 10UF 50V X7R 1210 | C1 C2 C3 C4 C11 C12 C13 C14 C15 C27 C29 C33 C34 C36 C41 C43 C45 C46 | Taiyo Yuden | UMK325AB7106KM-T | DK | 587-3167-6-ND | $0.66 | $10.62
16 | 10R0 | RES SMD 10 OHM 1% 1/4W 1206 | R23 R27 R32 R34 R36 R37 R38 R39 R45 R47 R51 R52 R54 R55 R56 R58 | Vishay | RCG120610R0FKEA | DK | 541-1851-1-ND | $0.12 | $1.97
4 | 68uH/1A | INDUCTOR_SMSRU8043 | L1 L2 L3 L4 | Bournes | SRU8043-680Y | DK | SRU8043-680YCT-ND | $0.10 | $0.40
4 | AD5624R-3 | IC DAC NANO 12BIT 1.25V 10-MSOP | U8 U9 U15 U19 | ADI | AD5624RBRMZ-3 | DK | AD5624RBRMZ-3-ND | $11.23 | $44.92 |  | 40 | $449.20
12 | OP237 | General Purpose Amplifier 1 Circuit SOT-23-5 | U1 U2 U3 U4 U5 U6 U13 U14 U16 U18 U20 U21 | TI | OPA237NA/3K | DK | 296-26265-1-ND | $1.52 | $18.24
4 | AP8802HSP-13 | IC LED DRIVER RGLTR DIM 1A 8SOIC | U7 U10 U17 U22 | Diodes | AP8802HSP-13 | DK | AP8802HSP-13DICT-ND | $2.43 | $9.72
4 | DLFS240L | DIODE_SCHOTTKYPWRDI-123 | D1 D2 D3 D5 | Diodes Inc | DFLS240-7 | DK | DFLS240-7DIDKR-ND | $0.25 | $1.00
64 | LED_RGBOVSPRGBCR4_HS | Red, Green, Blue (RGB) 625nm Red, 525nm Green, 465nm | RGB1 - RGB64 | TT Electronics | OVSPRGBCR4 | DK | 365-1393-1-ND | $5.24 | $335.36
12 | NPN_DUALLFPAK56_BIGHS | NPN_DUALLFPAK56_BIGHS | Q1 Q2 Q3 Q4 Q5 Q6 Q7 Q8 Q9 Q10 Q11 Q12 | NXP | PHPT610035NKX | DK | 568-12554-1-ND | $0.89 | $10.68
1 | 74LVC1G3157 | IC SWITCH SPDT SOT23-6 | U11 | TI | SN74LVC1G3157DBVR | DK | 296-14908-1-ND | $0.37 | $0.37
1 | Header, RA, SM, 3pos | CONN HEADER 3POS R/A SMD GOLD | J1 | TE | 5-147278-2 | DK | A100890CT-ND | $4.33 | $4.33 | Need to remove mounts, for modular interface, can be left off
1 | Header, vert, SM, 3 pos | CONN HEADR 3POS IDC SMD GOLD | J3 | TE | 5-1375582-2 | DK | 5-1375582-2-ND | $1.58 | $1.58 | for modular interface, can be left off
2 | Header, vert, SM, 3 pos | CONN HEADER 3POS VERT .100 GOLD | J4 J6 | TE | 3-647167-3 | DK | 3-647167-3-ND | $1.76 | $3.52
1 | LM26 | IC THERMOSTAT PRESET SOT-23-5 50 deg | U12 | TI | LM26CIM5-PHA/NOPB | DK | 296-35575-6-ND | $1.77 | $1.77
4 | Ferrite bead | FERRITE BEAD 600 OHM 0805 1LN | I1 I2 I3 I4 | Bournes | MH2029-601Y | DK | MH2029-601YCT-ND | $0.10 | $0.40
 |  |  |  |  |  |  |  |  | $610.04

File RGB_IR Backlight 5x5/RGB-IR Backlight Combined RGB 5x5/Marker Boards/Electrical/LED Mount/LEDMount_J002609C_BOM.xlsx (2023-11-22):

J002607C
Qty | Value | Device | Designators | Manufacturer | Man PN | Vendor | Vendor PN | $ea | $Total | Notes
3 | LED | EMITTER IR 860NM 100MA SMD | D1 D2 D3 | ams-OSRAM USA INC. | SFH 4050-Z | DK | 475-SFH4050-ZCT-ND | $0.89
 |  |  |  |  |  |  |  |  | $0.00

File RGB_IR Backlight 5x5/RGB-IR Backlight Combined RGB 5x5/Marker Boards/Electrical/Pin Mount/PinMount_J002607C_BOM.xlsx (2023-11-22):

J002607C
Qty | Value | Device | Designators | Manufacturer | Man PN | Vendor | Vendor PN | $ea | $Total | Notes
4 | Spring Pin | CONTACT SPRING LOADED T/H GOLD | GND BLU GRN RED | Mill-Max Manufacturing Corp. | 0851-0-15-20-82-14-11-0 | DK | ED90512-ND | $1.36
1 | Header | CONN HEADER VERT 4POS 1.25MM | J5 | Hirose | DF13-4P-1.25DSA | DK | H2193-ND | $0.42
2 | Housing | CONN RCPT HSG 4POS 1.25MM |  | Hirose | DF13-4S-1.25C | DK | H2181-ND | $0.18
1 | Cable Assembly | Black 28 AWG Jumper Lead Socket to Socket Tin 12.0" (304.8mm) |  | Hirose | H4BBT-10112-B8 | DK | H4BBT-10112-B8-ND | $0.63
1 | Cable Assembly | Red 28 AWG Jumper Lead Socket to Socket Tin 12.0" (304.8mm) |  | Hirose | H4BBT-10112-R8 | DK | H4BBT-10112-R8-ND | $0.63
1 | Cable Assembly | Blue 28 AWG Jumper Lead Socket to Socket Tin 12.0" (304.8mm) |  | Hirose | H4BBT-10112-L8 | DK | H4BBT-10112-L8-ND | $0.63
1 | Cable Assembly | Green 28 AWG Jumper Lead Socket to Socket Tin 12.0" (304.8mm) |  | Hirose | H4BBT-10112-G8 | DK | H4BBT-10112-G8-ND | $0.63
 |  |  |  |  |  |  |  |  | $0.00

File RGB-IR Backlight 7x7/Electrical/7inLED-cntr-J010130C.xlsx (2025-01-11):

7x7RGB-IR-J010129C
Qty | Value | Device | Designators | Manufacturer | Man PN | Vendor | Vendor PN | $ea | $Total | Notes
1 | BNC | BNC Connector Jack, Female Socket 50Ohm Through Hole Solder | J3 | Amphenol RF | 112404 | DK | ACX1051-ND | $4.44
2 |  | CONN HEADER VERT 3POS 2.54MM | J7 J8 | TE Connectivity AMP Connectors | 5-104362-2 | DK | 5-104362-2-ND | $1.66
1 |  | CONN HEADER VERT 3POS 1.25MM | J1 | Molex | 0530470310 | DK | WM1732-ND | $0.27
1 |  | CONN HEADER VERT 4POS 1.25MM | J2 | Molex | 0530470410 | DK | WM1733-ND | $0.34
2 |  | CONN HDR 16POS 0.1 GOLD PCB | P1 P2 | Sullins Connector Solutions | SFH11-PBPC-D08-ST-BK | DK | S9196-ND | $1.04
1 |  | DC DC CONVERTER 5V 3W | PS1 | Traco Power | TDN 3-2411WISM | DK | TDN3-2411WISM-ND | $24.72
1 |  | INDUCTOR0805S | I1 |  |  | DK
1 |  | M04LOCK | GND |  |  | DK
11 | 0.1 | CAPS0603S | C2 C3 C5 C7 C8 C9 C10 C13 C14 C16 C18 |  |  | DK
1 | 0.01 | CAPS0805S | C1 |  |  | DK
1 | 2G17 | IC BUF NON-INVERT 5.5V SOT23-6 | U9 | Texas Instruments | SN74LVC2G17DBVT | DK | 296-26621-1-ND | $1.32
5 | 6.8 | CAPS1206S | C4 C11 C12 C15 C17 |  |  | DK
2 | 3K30 | RES ARRAY 6 RES 3.3K OHM 7SIP | RN1 RN2 | Bourns Inc. | 4607X-101-332LF | DK | 4607X-101-332LF-ND | $0.50
2 | 100 | RESISTOR_SM0805S | R5 R6 |  |  | DK
4 | 332 | RESISTOR_SM0805S | R1 R2 R3 R4 |  |  | DK
1 | 741G3157DBVR | IC SWITCH SPDT SOT23-6 | U8 | Texas Instruments | SN74LVC1G3157DBVR | DK | 296-14908-1-ND | $0.50
1 | AD5624R-3 | IC DAC 12BIT V-OUT 10MSOP | U2 | Analog Devices Inc. | AD5624RBRMZ-3 | DK | 505-AD5624RBRMZ-3-ND | $13.00
1 | CON2X3 | CON2X3 | P3 |  |  | DK
1 | Diode | Diode Schottky 40 V 2A Surface Mount PowerDI™ 123 | D1 | Diodes Incorporated | DFLS240-7 | DK | DFLS240-7DICT-ND | $0.60
1 | IL 710 | DGTL ISO 2500VRMS 1CH GP 8MSOP | U24 | NVE Corp/Isolation Products | IL 710S-1E | DK | 390-IL710S-1E-ND | $5.70
1 | 3.3V regulator | IC REG LIN 3.3V 100MA TSOT23-5 | U1 | Analog Devices Inc. | LT1761ES5-3.3#TRPBF | DK | 505-LT1761ES5-3.3#TRPBFCT-ND | $3.20 |  | or LD2985BM33R
4 | OPA4197IDR | QUAD_OPAMPD | U3 U4 U5 U6 | Texas Instruments | LMV344MAX/NOPB | DK | LMV344MAX/NOPBCT-ND | $1.66 |  | or LMP2234
1 |  | CONN HEADER VERT 5POS 2.54MM | J4 | TE Connectivity AMP Connectors | 5-104362-4 | DK | A33971-ND | $2.66
1 | Teensy 4.0 | TEENSY 4.0 (HEADERS) | M1 | SparkFun Electronics | DEV-16997 | DK | 1568-DEV-16997-ND | $28.50 |  | Plug in after board is complete
 | TOTAL |  |  |  |  |  |  | $90.11

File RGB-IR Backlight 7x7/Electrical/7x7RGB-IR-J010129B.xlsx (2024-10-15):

J007017_RGB_IR
Qty | Value | Device | Designators | Manufacturer | Man PN | Vendor | Vendor PN | $ea | $Total | Notes | X10 | $x10 | x3
3 |  | 47µF 63V Aluminum Capacitors Radial, Can - SMD 2000 Hrs @ 85°C | C1 C10 C19 | Nichicon | UUR1J470MNL1GS | DK | 493-6235-1-ND | $0.52 | $1.56 |  | 30 | $15.60 | $4.68
259 |  | Infrared (IR) Emitter 860nm 1.5V 100mA 9mW/sr @ 100mA 140° 2-SMD, Flat Lead | D1 D2 D3 D4 D5 D6 D7 D8 D9 D10 D11 D12 D13 D14 D15 D16 D17 D18 D19 D20 D21 D22 D23 D24 D25 D26 D27 D28 D29 D30 D31 D32 D33 D34 D35 D36 D37 D38 D39 D40 D41 D42 D43 D44 D45 D46 D47 D48 D50 D51 D52 D53 D54 D55 D56 D57 D58 D59 D60 D61 D62 D63 D64 D65 D66 D67 D68 D69 D70 D71 D72 D73 D74 D75 D76 D77 D78 D79 D80 D81 D83 D84 D85 D86 D87 D88 D89 D90 D91 D92 D93 D94 D95 D96 D97 D98 D99 D100 D101 D102 D103 D104 D105 D106 D107 D108 D109 D110 D111 D112 D113 D114 D115 D116 D117 D118 D119 D120 D121 D122 D123 D124 D125 D126 D127 D128 D129 D130 D131 D132 D133 D134 D135 D136 D137 D138 D139 D140 D141 D142 D143 D144 D145 D146 D147 D148 D149 D150 D151 D152 D153 D154 D155 D156 D157 D158 D159 D160 D161 D162 D163 D164 D165 D166 D167 D168 D169 D170 D171 D172 D173 D174 D175 D176 D177 D178 D180 D181 D182 D183 D184 D185 D186 D187 D188 D189 D190 D191 D192 D193 D194 D195 D196 D197 D198 D199 D200 D201 D202 D203 D204 D205 D206 D207 D208 D209 D210 D211 D213 D214 D215 D216 D217 D218 D219 D220 D221 D222 D223 D224 D225 D226 D227 D228 D229 D230 D231 D232 D233 D234 D235 D236 D237 D238 D239 D240 D241 D242 D243 D244 D245 D246 D247 D248 D249 D250 D251 D252 D253 D254 D255 D256 D257 D258 D259 D260 D261 D262 D263 | OSRAM | SFH 4050-Z | DK | 475-2864-1-ND |  | $0.00 |  | 2590 | $0.00 | $0.00
1 |  | POWER_JACK_SHUNTPJ-002 | J1 | CUI | PJ-002BH-SMT-TR | DK | CP-002BHPJCT-ND | $1.89 | $1.89 |  | 10 | $18.90 | $5.67
4 | 0.1 | CAP CER 0.1UF 50V X7R 0603 | C2 C8 C11 C17 | Kemet | C0603C104K5RACTU | DK | 399-5089-1-ND | $0.03 | $0.11 |  | 40 | $1.12 | $0.34
4 | 1R00 | RES SMD 1 OHM 1% 1/4W 1206 | R16 R19 R50 R53 | Vishay | RCA12061R00FKEA | DK | 541-2240-1-ND | $0.13 | $0.52 |  | 40 | $5.20 | $1.56
8 | 2.2@50 | CAP CER 2.2UF 100V X7S 1206 | C4 C5 C6 C9 C13 C14 C15 C18 | TDK | C3216X7S2A225K160AB | DK | 445-5207-1-ND | $0.57 | $4.56 |  | 80 | $45.60 | $13.68
4 | 4.99K | RES SMD 4.99K OHM 1% 1/2W 0805 | R14 R20 R48 R54 | Stackpole Electronics Inc | RNCP0805FTD4K99 | DK | RNCP0805FTD4K99CT-ND | $0.24 | $0.96 |  | 40 | $9.60 | $2.88
24 | 4R99 | 4.99 Ohms ±1% 1W Chip Resistor 2512 (6432 Metric) Automotive AEC-Q200 Thick Film | R3 R5 R7 R10 R11 R13 R22 R24 R25 R27 R29 R32 R37 R39 R41 R44 R45 R47 R56 R58 R59 R61 R63 R66 | Stackpole Electronics Inc | RMCF2512FT4R99 | DK | RMCF2512FT4R99CT-ND | $0.34 | $8.16 |  | 240 | $81.60 | $24.48
4 | 10@50 | CAP CER 10UF 50V X7R 1210 | C3 C7 C12 C16 | Taiyo Yuden | UMK325AB7106KM-T | DK | 587-3167-6-ND | $0.66 | $2.66 |  | 40 | $26.56 | $7.97
16 | 10R0 | RES SMD 10 OHM 1% 1/4W 1206 | R1 R4 R9 R12 R23 R26 R30 R34 R35 R38 R43 R46 R57 R60 R64 R67 | Vishay | RCG120610R0FKEA | DK | 541-1851-1-ND | $0.12 | $1.97 |  | 160 | $19.68 | $5.90
4 | 68uH/1A | INDUCTOR_SMSRU8043 | L1 L2 L3 L4 | Bournes | SRU8043-680Y | DK | SRU8043-680YCT-ND | $0.10 | $0.40 |  | 40 | $4.00 | $1.20
4 | LED Driver IC 1 Output DC DC Regulator Step-Down (Buck) Analog, PWM Dimming 1A (Switch) 8-SO-EP |  | U1 U2 U3 U4 | Diodes Incorporated | AP8802HSP-13 | DK | AP8802HSP-13DICT-ND | 2.38 | $9.52 |  |  |  | $28.56
4 | DLFS240L | DIODE_SCHOTTKYPWRDI-123 | D49 D82 D179 D212 | Diodes Inc | DFLS240-7 | DK | DFLS240-7DIDKR-ND | $0.25 | $1.00 |  | 40 | $10.00 | $3.00
12 | NPN_DUALLFPAK56_BIGHS | NPN_DUALLFPAK56_BIGHS | Q1 Q2 Q3 Q4 Q5 Q6 Q7 Q8 Q9 Q10 Q11 Q12 | NXP | PHPT610035NKX | DK | 568-12554-1-ND | $0.89 | $10.68 |  | 120 | $106.80 | $32.04
14 | jumper | 2 (1 x 2) Position Shunt Connector Non-Insulated 0.319" (8.10mm) Tin | JMP1 JMP2 JMP4 JMP5 JMP6 JMP7 JMP8 JMP9 JMP10 JMP11 JMP12 JMP13 JMP14 JMP15 | Keystone Electronics | 5100 | DK | 36-5100-ND | $0.24 | $3.36 |  | 140 | $33.60 | $10.08
18 | 0 ohm 1206 | 0 Ohms Jumper 0.25W, 1/4W Chip Resistor 1206 (3216 Metric) Automotive AEC-Q200 Thick Film | R2 R6 R8 R17 R18 R21 R28 R31 R33 R36 R40 R42 R51 R52 R55 R62 R65 R68 | Stackpole Electronics Inc | RMCF1206ZT0R00 | DK | RMCF1206ZT0R00CT-ND | $0.10 | $1.80 |  | 180 | $18.00 | $5.40
1 | 0 ohm 2010 | 0 Ohms Jumper 0.75W, 3/4W Chip Resistor 2010 (5025 Metric) Automotive AEC-Q200 Thick Film | R49 | Stackpole Electronics Inc | RMCF2010ZT0R00 | DK | RMCF2010ZT0R00CT-ND | $0.21 | $0.21 |  | 10 | 2.1 | $0.63
2 | 2x8 header | Connector Header Surface Mount 16 position 0.100" (2.54mm) | P1 P2 | Assmann WSW Components | AWHW 16G-SMD | DK | AE11242-ND | $1.50 | $3.00 | Triangle on part goes to small circle on board by pin 1 | 20 | 30 | $9.00
64 | RED LED | High Power LEDs - Single Color Red | RGB1-64 | Lumileds | L1C1-RED1000000000 |  |  | $1.57 | $100.48 |  | 640 | 1004.8 | $301.44
64 | BLUE LED | High Power LEDs - Single Color Blue 460nm-480nm | RGB1-65 |  | L1C1-BLU1000000000 |  |  | $1.14 | $72.96 |  | 640 | 729.6 | $218.88
64 | GREEN LED | High Power LEDs - Single Color Green -540nm | RGB1-66 |  | L1C1-GRN1000000000 |  |  | $1.14 | $72.96 |  | 640 | $729.60 | $218.88
 |  | NOTE: Place LEDS at each location using silkscreen markings 'R', 'G', 'B'. |  |  |  |  |  |  |  |  |  |  | 350 | PCB
1 | 2x3 header | Connector Header Surface Mount 6 position 0.100" (2.54mm) | P4 | Samtec Inc. | HTSS-103-01-T-DV | DK | HTSS-103-01-T-DV-ND | $3.06 | $3.06 |  | 10 | $30.60 | $9.18
 |  |  |  |  |  |  |  |  | $298.76 |  |  |  | $1255.45

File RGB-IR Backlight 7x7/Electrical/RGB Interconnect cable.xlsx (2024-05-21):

RGB Interconnect Cable
Qty | Value | Device | Designators | Manufacturer | Man PN | Vendor | Vendor PN | $ea | $Total | Notes
2 | 3 Pin Connector | 3 Rectangular Connectors - Housings Receptacle Black 0.100" (2.54mm) | J1 J2 | TE Connectivity AMP Connectors | 104257-2 | DK | A28397-ND | 0.55
6 | terminal | CONN SOCKET 22-26AWG CRIMP GOLD |  | TE Connectivity AMP Connectors | 1-104480-5 | DK | A32512-ND | 0.26
As Required | Wire | 24AWG Black stranded hook up wire
As Required | Wire | 24AWG Red stranded hook up wire
As Required | Wire | 24AWG Gray stranded hook up wire
TOOL |  | crimper |  | TE Application Tooling | 91518-1 | DK | A29087-ND

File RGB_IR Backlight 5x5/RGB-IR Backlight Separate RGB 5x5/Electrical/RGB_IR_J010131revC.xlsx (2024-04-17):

J010131 RGB_IR REV C
 |  |  |  |  |  |  |  |  |  |  | X10 | $x10
Qty | Value | Device | Designators | Manufacturer | Man PN | Vendor | Vendor PN | $ea | $Total | Notes
3 |  | 47µF 63V Aluminum Capacitors Radial, Can - SMD 2000 Hrs @ 85°C | C20 C21 C43 | Nichicon | UUR1J470MNL1GS | DK | 493-6235-1-ND | $0.52 | $1.56 |  | 30 | $15.60
1 |  | CONN HEADER 3POS 1.25MM SMD GOLD | J5 | Molex | 533984003 | DK | 900-0533984003CT-ND | $0.85 | $0.85 |  | 10 | $8.50
256 |  | Infrared (IR) Emitter 860nm 1.5V 100mA 9mW/sr @ 100mA 140° 2-SMD, Flat Lead | IR1-IR256 | OSRAM | SFH 4050-Z | DK | 475-2864-1-ND |  | $0.00 |  | 2560 | $0.00
1 |  | POWER_JACK_SHUNTPJ-002 | J1 | CUI | PJ-002BH-SMT-TR | DK | CP-002BHPJCT-ND | $1.89 | $1.89 |  | 10 | $18.90
2 |  | CONN RCPT .100" 14POS SNGL VERT | M1A M1B | Samtec | SSM-114-L-SV | DK | SAM1148-14-ND | $4.42 | $8.84 | socket for M1 | 20 | $88.40
1 |  | TEENSY 4.0 (HEADERS) | M1 | Sparkfun | DEV-16997 | DK | 1568-DEV-16997-ND | $28.50 | $28.50 |  | 10 | $285.00
25 | 0.1 | CAP CER 0.1UF 50V X7R 0603 | C5 C6 C7 C8 C9 C10 C11 C12 C18 C19 C22 C24 C25 C30 C31 C33 C36 C37 C38 C44 C45 C47 C49 C51 C52 | Kemet | C0603C104K5RACTU | DK | 399-5089-1-ND | $0.03 | $0.70 |  | 250 | $7.00
4 | 1R00 | RES SMD 1 OHM 1% 1/4W 1206 | R23 R26 R49 R69 | Vishay | RCA12061R00FKEA | DK | 541-2240-1-ND | $0.13 | $0.52 |  | 40 | $5.20
4 | 2.2@50 | CAP CER 2.2UF 100V X7S 1206 | C27 C28 C40 C55 | TDK | C3216X7S2A225K160AB | DK | 445-5207-1-ND | $0.57 | $2.28 |  | 40 | $22.80
4 | 4.99K | RES SMD 4.99K OHM 1% 1/2W 0805 | R19 R24 R48 R68 | Vishay | CRCW08054K99FKEAHP | DK | 541-4.99KTCT-ND | $0.24 | $0.96 |  | 40 | $9.60
1 | 100 | RES SMD 100 OHM 1% 1/2W 0805 | R29 | Vishay | CRCW0805100RJNEA | DK | 541-100ACT-ND | $0.10 | $0.10 |  | 10 | $1.00
4 | 332 | RES SMD 332 OHM 1% 1/8W 0805 | R17 R18 R22 R31 | Vishay | CRCW0805332RFKEA | DK | 541-332CCT-ND | $0.10 | $0.40 |  | 40 | $4.00
24 | 4R99 | RES SMD 4.99 OHM 1W 1812 WIDE | R1 R2 R3 R4 R5 R6 R7 R8 R9 R10 R11 R12 R30 R32 R35 R36 R40 R42 R50 R51 R55 R56 R64 R65 | Vishay | RCL12184R99FKEK | DK | 541-2430-1-ND |  | $0.00 |  | 240 | $0.00
19 | 10@50 | CAP CER 10UF 50V X7R 1210 | C1 C2 C3 C4 C13 C14 C15 C16 C17 C29 C32 C34 C39 C41 C42 C48 C50 C53 C54 | Taiyo Yuden | UMK325AB7106KM-T | DK | 587-3167-6-ND | $0.66 | $12.62 |  | 190 | $126.16
16 | 10R0 | RES SMD 10 OHM 1% 1/4W 1206 | R28 R33 R38 R41 R43 R44 R45 R46 R52 R53 R57 R59 R60 R61 R62 R63 | Vishay | RCG120610R0FKEA | DK | 541-1851-1-ND | $0.12 | $1.97 |  | 160 | $19.68
4 | 68uH/1A | INDUCTOR_SMSRU8043 | L1 L2 L3 L4 | Bournes | SRU8043-680Y | DK | SRU8043-680YCT-ND | $0.10 | $0.40 |  | 40 | $4.00
4 | AD5624R-3 | IC DAC NANO 12BIT 1.25V 10-MSOP | U10 U11 U16 U20 | ADI | AD5624RBRMZ-3 | DK | AD5624RBRMZ-3-ND | $1.23 | $4.92 |  | 40 | $49.20
12 | OP237 | General Purpose Amplifier 1 Circuit SOT-23-5 | U1 U3 U4 U5 U6 U7 U14 U15 U17 U19 U21 U23 | TI | OPA237NA/3K | DK | 296-26265-1-ND | $1.52 | $18.24 |  | 120 | $182.40
4 | AP8802HSP-13 | IC LED DRIVER RGLTR DIM 1A 8SOIC | U9 U12 U18 U24 | Diodes | AP8802HSP-13 | DK | AP8802HSP-13DICT-ND | $2.43 | $9.72 |  | 40 | $97.20
5 | DLFS240L | DIODE_SCHOTTKYPWRDI-123 | D1 D2 D3 D4 D5 | Diodes Inc | DFLS240-7 | DK | DFLS240-7DIDKR-ND | $0.25 | $1.25 |  | 50 | $12.50
12 | NPN_DUALLFPAK56_BIGHS | NPN_DUALLFPAK56_BIGHS | Q1 Q2 Q3 Q4 Q5 Q6 Q7 Q8 Q9 Q10 Q11 Q12 | NXP | PHPT610035NKX | DK | 568-12554-1-ND | $0.89 | $10.68 |  | 120 | $106.80
1 | 74LVC1G3157 | IC SWITCH SPDT SOT23-6 | U8 | TI | SN74LVC1G3157DBVR | DK | 296-14908-1-ND | $0.37 | $0.37 |  | 10 | $3.70
2 | Header, vert, SM, 3 pos | CONN HEADER 3POS VERT .100 GOLD | J4 J6 | TE | 3-647167-3 | DK | 3-647167-3-ND | $1.76 | $3.52 |  | 20 | $35.20
1 | LM26 | IC THERMOSTAT PRESET SOT-23-5 50 deg | U13 | TI | LM26CIM5-PHA/NOPB | DK | 296-35575-6-ND | $1.77 | $1.77 |  | 10 | $17.70
12 | 49K9 resistor | 49.9 ±1% 0.25W, 1/4W Chip Resistor 1206 (3216 Metric) Automotive AEC-Q200 Thick Film | R13 R14 R15 R16 R20 R21 R34 R37 R47 R54 R58 R67 | Stackpole Electronics Inc | RMCF1206FT49K9 | DK | RMCF1206FT49K9CT-ND | $0.10 | $1.20 |  | 120 | $12.00
1 | buffer | Buffer, Non-Inverting 1 Element 1 Bit per Element Push-Pull Output SOT-23-5 | U2 | Texas Instruments | SN74AUC1G17DBVR | DK | 296-12654-1-ND | $0.50 | $0.50 |  | 10 | 5
1 | 4 pos header | CONN HEADER SMD 4POS 1.25MM | J3 | Molex | 533984004 | DK | 900-0533984004CT-ND | $1.02 | $1.02 |  | 10 | 10.2
1 | SMA | SMA Connector Receptacle, Female Socket 50Ohm Surface Mount, Right Angle Solder | J2 | Linx Technologies Inc. | CONSMA002-SMD-G | DK | CONSMA002-SMD-G-ND | $4.26 | $4.26 |  | 10 | 42.6
64 | BLUE LED | LED LUXEON C BLUE 475NM SMD | LB1 LB2 LB3 LB4 LB5 LB6 LB7 LB8 LB9 LB10 LB11 LB12 LB13 LB14 LB15 LB16 LB17 LB18 LB19 LB20 LB21 LB22 LB23 LB24 LB25 LB26 LB27 LB28 LB29 LB30 LB31 LB32 LB33 LB34 LB35 LB36 LB37 LB38 LB39 LB40 LB41 LB42 LB43 LB44 LB45 LB46 LB47 LB48 LB49 LB50 LB51 LB52 LB53 LB54 LB55 LB56 LB57 LB58 LB59 LB60 LB61 LB62 LB63 LB64 | Lumileds | L1C1-BLU1000000000 | DK | 1416-1698-1-ND | $1.13 | $72.32 |  | 640 | 723.2
64 | DEEP RED LED | LED LUXEON C DEEP RED 475NM SMD | LR1 LR2 LR3 LR4 LR5 LR6 LR7 LR8 LR9 LR10 LR11 LR12 LR13 LR14 LR15 LR16 LR17 LR18 LR19 LR20 LR21 LR22 LR23 LR24 LR25 LR26 LR27 LR28 LR29 LR30 LR31 LR32 LR33 LR34 LR35 LR36 LR37 LR38 LR39 LR40 LR41 LR42 LR43 LR44 LR45 LR46 LR47 LR48 LR49 LR50 LR51 LR52 LR53 LR54 LR55 LR56 LR57 LR58 LR59 LR60 LR61 LR62 LR63 LR64 | Lumileds | L1C1-DRD1000000000 | DK |  | $1.13 | $72.32 |  | 640 | 723.2
64 | GREEN LED | LED LUXEON C GREEN 530NM SMD | LG1 LG2 LG3 LG4 LG5 LG6 LG7 LG8 LG9 LG10 LG11 LG12 LG13 LG14 LG15 LG16 LG17 LG18 LG19 LG20 LG21 LG22 LG23 LG24 LG25 LG26 LG27 LG28 LG29 LG30 LG31 LG32 LG33 LG34 LG35 LG36 LG37 LG38 LG39 LG40 LG41 LG42 LG43 LG44 LG45 LG46 LG47 LG48 LG49 LG50 LG51 LG52 LG53 LG54 LG55 LG56 LG57 LG58 LG59 LG60 LG61 LG62 LG63 LG64 | Lumileds | L1C1-GRN1000000000 | DK | 1416-1914-1-ND | $1.13 | $72.32 |  | 640 | 723.2
4 | 4R99 resistor | RES SMD 4.99 OHM 1% 1/8W 0805 | R25 R27 R39 R66 | Vishay Dale | CRCW08054R99FNEA | DK | 541-4.99CCT-ND | $0.12 | $0.48 |  | 40 | 4.8
1 | 1 ch isolator | DGTL ISO 2500VRMS 1CH GP 8SOIC | U22 | Analog Devices Inc. | ADUM1100ARZ-RL7 | DK | ADUM1100ARZ-RL7CT-ND | $4.44 | $4.44 |  | 10
4 | 4.7uF Capacitor | CAP CER 4.7UF 35V X7R 0805 | C23 C26 C35 C46 | TDK Corporation | C2012X7R1V475K125AC | DK | 445-7555-1-ND | $0.57 | $2.28 |  | 40
1 | dc-dc | DC DC CONVERTER 5V 1W | PS1 | Traco Power | TDN 1-2411WISM | DK | TDN1-2411WISM-ND | $18.38 | $18.38 |  | 10
RED | 20 | 0.4
GREEN | 30 | 0.6
BLUE | 20 | 0.4
IR | 50 | 0.8
 |  | 2.2
 |  |  |  |  |  |  |  |  | $361.57
 | Power supplies | Desktop AC Adapters 160W 28V 5.7A 2.5mm straight |  | Cincon | TRH160A280-12E13 VI | Mouser | 418-TRH160A2801213VI | $54.00
 | Heat sinks
 | Finned Heat Sink |  |  | AAVID | 601403B06000 | Newark | 93H3803 | $52.81 |  | 6" length, machine 25 threaded holes
 | Liquid cooled Heat Sink |  |  | AAVID | 416101U00000G | DK | 416101U00000G-ND | $61.64 |  | Mount to non-pipe side with 25 depth limited threaded holes
 |  |  |  | Berqquist | GPHC5.0-0.020-02-0816 | DK | BER369-ND | $57.93 |  | cut to size; 2 per sheet

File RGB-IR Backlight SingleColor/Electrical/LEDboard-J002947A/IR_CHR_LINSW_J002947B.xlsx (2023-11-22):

Partlist exported from C:/_Workspace/DATA/PROJECTS/FLY_BOWL_LEDS/ECAD/Linear-Switched/IR_CHR_LINSW_J002947B.sch at 4/5/2015 10:35:37 AM
Qty | Value | Device | Designators | Manufacturer | Man PN | Vendor | Vendor PN | 20 boards |  | $/ | $/board
1 |  | CON2DF3-2\ | J2 | Hirose | DF3DZ-2P-2H(51) | Digi-Key | HR1990DKR-ND | 20 | DF3DZ-2P-2H(51) | $0.84 | $0.84
1 |  | DIODE_ARRAY_4X_CC | D261 | Toshiba | 1SS309(TE85L,F) |  |  | 20 | 1SS309(TE85L,F) | $0.48 | $0.48
256 |  | LEDLED_SFH4050_HEAT | D3 D4 D5 D6 D7 D8 D9 D10 D11 D12 D13 D14 D15 D16 D17 D18 D19 D20 D21 D22 D23 D24 D25 D26 D27 D28 D29 D30 D31 D32 D33 D34 D35 D36 D37 D38 D39 D40 D41 D42 D43 D44 D45 D46 D47 D48 D49 D50 D51 D52 D53 D54 D55 D56 D57 D58 D59 D60 D61 D62 D63 D64 D65 D66 D67 D68 D69 D70 D71 D72 D73 D74 D75 D76 D77 D78 D79 D80 D81 D82 D84 D85 D86 D87 D88 D89 D90 D91 D92 D93 D94 D95 D96 D97 D98 D99 D100 D101 D102 D103 D104 D105 D106 D107 D108 D109 D110 D111 D112 D113 D114 D115 D116 D117 D118 D119 D120 D121 D122 D123 D124 D125 D126 D127 D128 D129 D130 D131 D132 D133 D134 D135 D136 D137 D138 D139 D140 D141 D142 D143 D144 D145 D146 D147 D148 D149 D150 D151 D152 D153 D154 D155 D156 D157 D158 D159 D160 D161 D162 D163 D164 D165 D166 D167 D168 D169 D170 D171 D172 D173 D174 D175 D176 D177 D178 D179 D180 D181 D182 D183 D184 D185 D186 D187 D188 D189 D190 D191 D192 D193 D194 D195 D197 D198 D199 D200 D201 D202 D203 D204 D205 D206 D207 D208 D209 D210 D211 D212 D213 D214 D215 D216 D217 D218 D219 D220 D221 D222 D223 D224 D225 D226 D227 D228 D229 D230 D231 D232 D233 D234 D235 D236 D237 D238 D239 D240 D241 D242 D243 D244 D245 D246 D247 D248 D249 D250 D251 D252 D253 D254 D255 D256 D257 D258 D259 D260 | Osram Opto | SFH 4050-Z | Digi-Key | 475-2864-1-ND | 5120 | SFH 4050-Z | $0.49 | $125.44
5 |  | MOSFET-N | Q5 Q6 Q8 Q9 Q12 | ON Semi | 2N7002WT1G |  | 2N7002WT1GOSTR-ND | 100 |  | $0.10 | $0.50
8 |  | MOSFET-NTI252_HS | Q1 Q2 Q3 Q4 Q10 Q11 Q13 Q14 | Fairchild | FQD10N20CTM |  | FQD10N20CTMDKR-ND | 160 | FQD10N20CTM | $0.52 | $4.16
2 |  | POWER_JACK_SHUNTPJ-002 | J1 J3 |  |  |  |  | 40 |  | $1.90 | $3.80
64 |  | REBEL_0603OG_LED_W0603_EVEN_12 | LED1 LED2 LED3 LED4 LED5 LED6 LED7 LED8 LED9 LED10 LED11 LED12 LED13 LED14 LED15 LED16 LED17 LED18 LED19 LED20 LED21 LED22 LED23 LED24 LED25 LED26 LED27 LED28 LED29 LED30 LED31 LED32 LED33 LED34 LED35 LED36 LED37 LED38 LED39 LED40 LED41 LED42 LED43 LED44 LED45 LED46 LED47 LED48 LED49 LED50 LED51 LED52 LED53 LED54 LED55 LED56 LED57 LED58 LED59 LED60 LED61 LED62 LED63 LED64 | Philips Lumileds | LXM2-PD01-0050 | Digi-Key | 1416-1024-1-ND | 1280 | LXM2-PD01-0050 | $1.52 | $97.28
15 | 0.1 | CAPS0603S | C1 C2 C3 C4 C7 C8 C11 C12 C13 C16 C17 C20 C22 C23 C24 | Kemet | C0603C104K5RACTU | Digi-Key | 399-5089-2-ND | 300 | C0603C104K5RACTU | $0.01 | $0.12
8 | 1R0 | RESISTOR-POWER2512_HS1 | R1 R2 R3 R4 R40 R50 R57 R67 | rohm | ESR18EZPF1R00 | digi-Key | RHM1.00AFTR-ND | 160 | ESR18EZPF1R00 | $0.02 | $0.16
4 | 1R00 | RESISTOR_SM1206S | R19 R20 R46 R62 | Vishay Dale | RCL12251R00FKEG | Digi-Key | RCL1.00ECT-ND | 80 | RCL12251R00FKEG | $0.20 | $0.80
4 | 2.2@50 | CAPS1206S | C9 C10 C15 C19 | Samsung | CL31A225KC9LNNC | Digi-Key | 1276-2724-1-ND | 80 | CL31A225KC9LNNC | $0.46 | $1.84
16 | 4.99K | RESISTOR_SM0603S | R12 R13 R21 R22 R23 R25 R35 R39 R49 R53 R56 R65 R16 R17 R45 R60 | Vishay Dale | RCG06034K99FKEA | digi-Key | 541-1783-2-ND | 320 | RCG06034K99FKEA | $0.01 | $0.16
21 | 10@50 | CAPS1210S | C5 C6 C14 C18 C21 C32 C33 C34 C35 C36 C37 C38 C39 C40 C41 C42 C43 C44 C45 C46 C47 | Murata | GRM31CR61H106KA12L | Digi-Key | 490-5961-1-ND | 420 | GRM31CR61H106KA12L | $0.15 | $3.15
5 | 10K | RESISTOR_SM0603S | R6 R24 R26 R30 R33 | Vishay Dale | RCG060310K0FKEA | Digi-Key | 541-1784-2-ND | 100 | RCG060310K0FKEA | $0.01 | $0.05
16 | 10R0 | RESISTOR_SM1206S | R28 R29 R38 R41 R42 R43 R44 R48 R52 R54 R58 R59 R61 R63 R66 R68 | Vishay Dale | RCG120610R0FKEA | Digi-Key | 541-1851-1-ND | 320 | RCG120610R0FKEA | $0.01 | $0.16
12 | 26.1K | RESISTOR_SM0603S | R14 R15 R37 R51 R36 R7 R9 R10 R11 R47 R55 R64 | Vishay Dale | CRCW060326K1FKEA | Digi-Key | 541-26.1KHTR-ND | 240 | CRCW060326K1FKEA | $0.01 | $0.12
4 | 68uH/1A | INDUCTOR_SMSRU8043 | L1 L2 L3 L4 | Bournes | SRU8043-680Y | Digi-Key | SRU8043-680YCT-ND | 80 | SRU8043-680Y | $0.33 | $1.32
2 | 74DUAL14 | 74DUAL14 | U10 U12 | TI | SN74LVC2G14DBVR | Digi-Key | 296-13010-6-ND | 40 | SN74LVC2G14DBVR | $0.17 | $0.34
6 | 100K | RESISTOR_SM0603S | R5 R18 R27 R31 R32 R34 | Vishay Dale | RCG0603100KFKEA | Digi-Key | 541-1788-2-ND | 120 | RCG0603100KFKEA | $0.01 | $0.06
2 | 499R | RESISTOR_SM0603S | R8 R69 | Vishay Dale | RCG0603499RFKEA | Digi-Key | 541-1779-2-ND | 40 | RCG0603499RFKEA | $0.01 | $0.02
1 | 7805DT | 7805DT | U13 | Fairchild | KA7805ERTM | Digi-Key | KA7805ERTMFSDKR-ND | 20 | KA7805ERTM | $0.28 | $0.28
10 | AD8613 | AD8065RT | U1 U2 U3 U4 U5 U8 U15 U17 U18 U20 | ti | OPA237NA/3K | Digi-Key | 296-26265-1-ND | 200 | OPA237NA/3K | $0.56 | $5.60
4 | AP8802 | AP8802 | U6 U21 U22 U23 | Diodes Inc | AP8802HSP-13 | Digi-Key | AP8802HSP-13DIDKR-ND | 80 | AP8802HSP-13 | $1.08 | $4.32
4 | DLFS240L | DIODE_SCHOTTKYPWRDI-123 | D1 D2 D83 D196 | Diodes Inc | DFLS240-7 | Digi-Key | DFLS240-7DIDKR-ND | 80 | DFLS240-7 | $0.25 | $1.00
2 | LM26 | LM26 | U9 U14 | TI | LM26CIM5-PHA/NOPB | Digi-Key | 296-35575-6-ND | 40 | LM26CIM5-PHA/NOPB | $0.48 | $0.96
1 | CONN HEADER 10POS SMD VERT 10AU | M05X22X5_SM_3M | JP1 | 3M | D2510-6V0C-AR-WD | Digi-Key | MSH10KCT-ND | 20 | D2510-6V0C-AR-WD | $1.53 | $1.53
1 | MAX9064 | MAX9064 | U11 | Maxim | MAX9064EUK+T | Digi-Key | MAX9064EUK+TDKR-ND | 20 | MAX9064EUK+T | $0.45 | $0.45
1 | MOSFET-P | MOSFET-P | Q7 | Vishay-Siliconix | SI7469DP-T1-E3 | Digi-Key | SI7469DP-T1-E3CT-ND | 20 | SI7469DP-T1-E3 | $1.03 | $1.03
1 | PCB |  |  |  |  |  |  |  |  | $44.00 | $44.00
1 | Assembly |  |  |  |  |  |  |  |  | $80.00 | $80.00
1 | 24V Power Supply |  |  | ITE | CENB1060A2403F01 |  |  |  |  | $35.99 | $35.99
1 | 36V Power Supply |  |  | CUI | ETMA360166UD |  |  |  |  | $50.48 | $50.48
 |  |  |  |  |  |  |  |  |  |  | $466.44

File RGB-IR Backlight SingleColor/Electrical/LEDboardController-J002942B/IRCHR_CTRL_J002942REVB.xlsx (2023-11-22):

Partlist exported from Z:/_Workspace/DATA/PROJECTS/FLY_BOWL_LEDS/ECAD/FlyBowlControl/IRCHR_CTRL_J002942REVB.sch at 5/15/2015 3:29:13 PM
BOM - J002942REVB
Qty | Value | Device | Designators | Manufacturer | Man PN | Vendor | Vendor PN | $ea | $Total | Notes
1 |  | CRYSTALCTS406 | X1 | CTS | 406C35D16M00000 | Digi-Key
1 |  | LEDCHIP-LED0805 | LED1 | Lite-On | LTST-C170YKT | Digi-Key |  | $0.36
1 |  | M04LOCK | JP8 |  |  | Digi-Key
1 |  | M05LOCK | JP4 |  |  | Digi-Key
1 |  | TAC_SWITCHSMD | S1 | Panasonic | EVQ-PLHA15 | Digi-Key |  | $0.65
4 | 0.1 | CAPS0805S | C1 C5 C6 C8 | Kemet | C0603C104K5RACTU | Digi-Key | 399-5089-2-ND | $0.01
3 | 1 | CAPS0805S | C3 C4 C7 | Kemet | C0805C105K5RACTU | Digi-Key |  | $0.34
2 | 1K | RESISTOR_SM0805S | R1 R2 | Vishay | CRCW08051K00FKEA | Digi-Key |  | $0.10
2 | 4.99K | RESISTOR_SM0805S | R5 R6 | Stackpole | RMCF0805FT4K99 | Digi-Key |  | $0.10
1 | 10 | CAPS1206S | C2 | Kemet | C1206C105K5RACTU | Digi-Key | 399-8147-1-ND | $0.28
1 | 10K | RESISTOR_SM0805S | R7 | Vishay | CRCW080510K0FKEAHP | Digi-Key | 541-10.0KTCT-ND | $0.30
2 | 18p | CAPS0805S | C9 C10 | AVX | 08051A180JAT2A | Digi-Key |  | $0.15
3 | 22 | RESISTOR_SM0805S | R3 R4 R8 | Vishay | CRCW080522R0FKEA | Digi-Key |  | $0.10
1 | 15912025 | CONN HEADER RT/A .100 2POS 15AU | J3 | TE Connectivity | 103635-1 | Digi-Key | WM1340-ND | $2.51
1 | AD5315 | DAC_AD53X5 | U3 | AD | AD5315ARMZ-REEL7 | Digi-Key |  | $8.26
1 | BNCPTH | BNCPTH | J1 |  |  |  |  |  |  | Not Installed
4 | D2510 | M05X22X5_SM_3M | JP1 JP2 JP6 JP7 | 3M | N2510-6V0C-RB-WD | Digi-Key | MSH10KDKR-ND | $2.26
1 | MC1525 | IC VREF SERIES 2.5V SOT23-3 | U2 | Microchip | MCP1525T-I/TT | Digi-Key | MCP1525T-I/TTCT-ND | $0.77
1 | TEENSY 2 | Atmel ATMEGA32U4 Chip with pre-programmed Halfkay bootloader | U1 |  | Teensy 2.0 IC | PJRC | IC_ATMEGA32U4_TQFP | $8.00
1 | UX60-MB-5ST | MINI-USB-UX60-MB-5ST | J2 | Hirose | UX60-MB-5ST | Digi-Key | H2959CT-ND | $0.94
1 | Cover plates | Acrylic top and bottom covers |  | HHMI | J002942REVB.DXF
1 | PCB |  |  | HHMI | J002942REVB |  |  | $22.30
AR | Cable | 10PIn Ribbon Cable |  | Samtec | FFSD-05-D-01.00-01-N |  |  | $15.53
 |  |  |  |  |  |  |  | $62.96

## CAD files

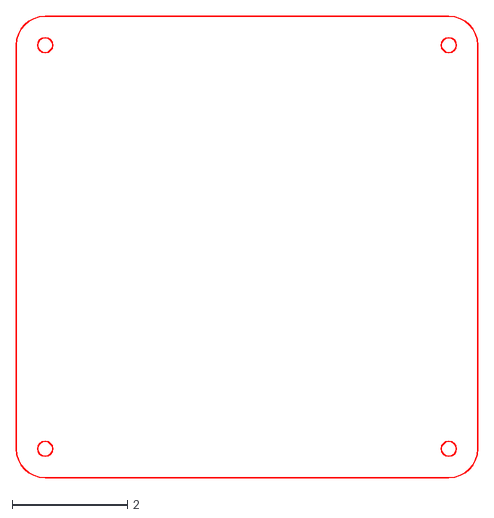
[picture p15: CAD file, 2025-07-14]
RGB_IR Backlight 5x5/Diffuser5x5.dxf
8.00 x 8.00

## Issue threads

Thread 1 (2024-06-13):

### ISSUE TITLE
BOM inaccuracies

### ISSUE THREAD

**Issue by phifisch** [janelia-experimental-technology/RGB-IR-LED-Boards#1]
Hello,

Thank you for your great work. I stumbled upon a few issues in the BOM when trying to have the board manufactured. For one U24 occurs twice. The second occurrence is the digital isolator, and should be changed to U22 to fit the schematic and placement file.
Also, U25, a 3.3V regulator  is mentioned only in the BOM, but does not appear in neither the schematic not the board design itself. Am I right to assume that the 3.3V rail is supposed to be supplied bythe Teensy board alone (so ultimately via the USB port?), and so a 3.3V regulator would be obsolete?

Cheers,
Phil

**Comment by sawtelles** [comment]
I’ll check into that. Thanks for letting me know.
-Steve

On Apr 17, 2024, at 6:14 AM, phifisch ***@***.***> wrote:

 
External Email: Use Caution



Hello,

Thank you for your great work. I stumbled upon a few issues in the BOM when trying to have the board manufactured. For one U24 occurs twice. The second occurrence is the digital isolator, and should be changed to U22 to fit the schematic and placement file.
Also, U25, a 3.3V regulator is mentioned only in the BOM, but does not appear in neither the schematic not the board design itself. Am I right to assume that the 3.3V rail is supposed to be supplied bythe Teensy board alone (so ultimately via the USB port?), and so a 3.3V regulator would be obsolete?

Cheers,
Phil

**Comment by sawtelles** [comment]
Hi Phil,

Fixed. Thanks for pointing it out!

I also added board specs – we use a 0.8mm board with 2oz copper with a white soldermask and black silkscreen. If you assemble the board yourself, you can order blank boards easily from Oshpark.

Also, you can use whatever colors you want for the LEDs as the package we use is available in many varieties. We have done RGB, red-green-green, deep red, etc.

Steve Sawtelle
Electrical Engineer
jET
Janelia, HHMI
19700 Helix Dr
Ashburn, VA  20147



From: phifisch ***@***.***>
Sent: Wednesday, April 17, 2024 6:14 AM
To: janelia-experimental-technology/RGB-IR-LED-Boards ***@***.***>
Cc: Subscribed ***@***.***>
Subject: [janelia-experimental-technology/RGB-IR-LED-Boards] BOM inaccuracies (Issue #1)

External Email: Use Caution


Hello,

Thank you for your great work. I stumbled upon a few issues in the BOM when trying to have the board manufactured. For one U24 occurs twice. The second occurrence is the digital isolator, and should be changed to U22 to fit the schematic and placement file.
Also, U25, a 3.3V regulator is mentioned only in the BOM, but does not appear in neither the schematic not the board design itself. Am I right to assume that the 3.3V rail is supposed to be supplied bythe Teensy board alone (so ultimately via the USB port?), and so a 3.3V regulator would be obsolete?

Cheers,
Phil

**Comment by phifisch** [comment]
Hi,
I forgot to feedback. Thanks for clarifying! Incidentally, thanks for adding the 7x7 as well.
Phil

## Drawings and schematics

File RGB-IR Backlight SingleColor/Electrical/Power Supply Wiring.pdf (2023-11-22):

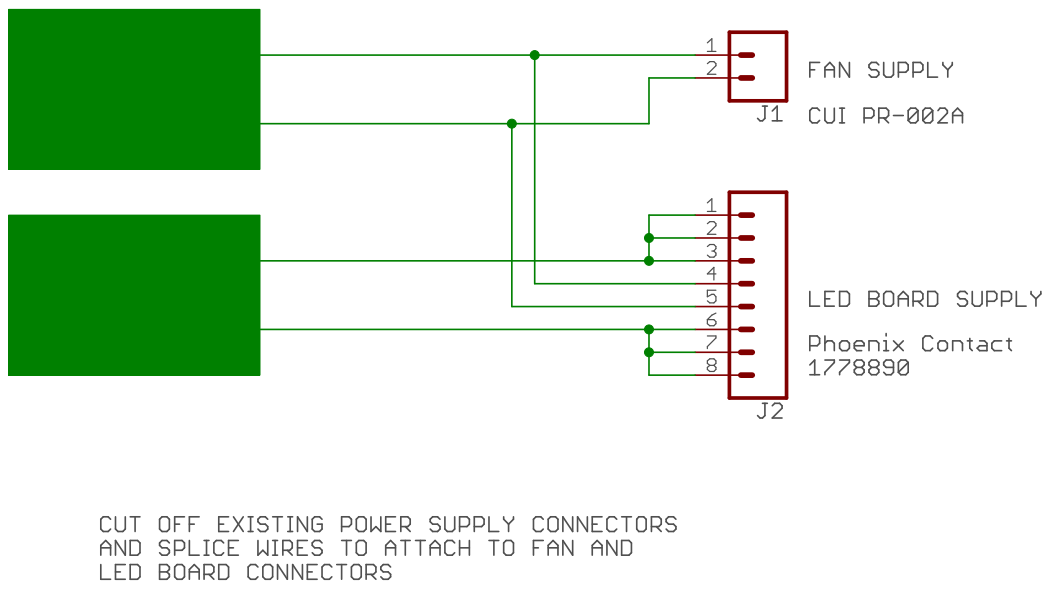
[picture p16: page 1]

11/15/2023 9:55 AM f=0.93 Z:\ASO\FLY_BOWL_LEDS\ECAD\PowerSplitter\PowerSupplyWiring.sch (Sheet: 1/1)

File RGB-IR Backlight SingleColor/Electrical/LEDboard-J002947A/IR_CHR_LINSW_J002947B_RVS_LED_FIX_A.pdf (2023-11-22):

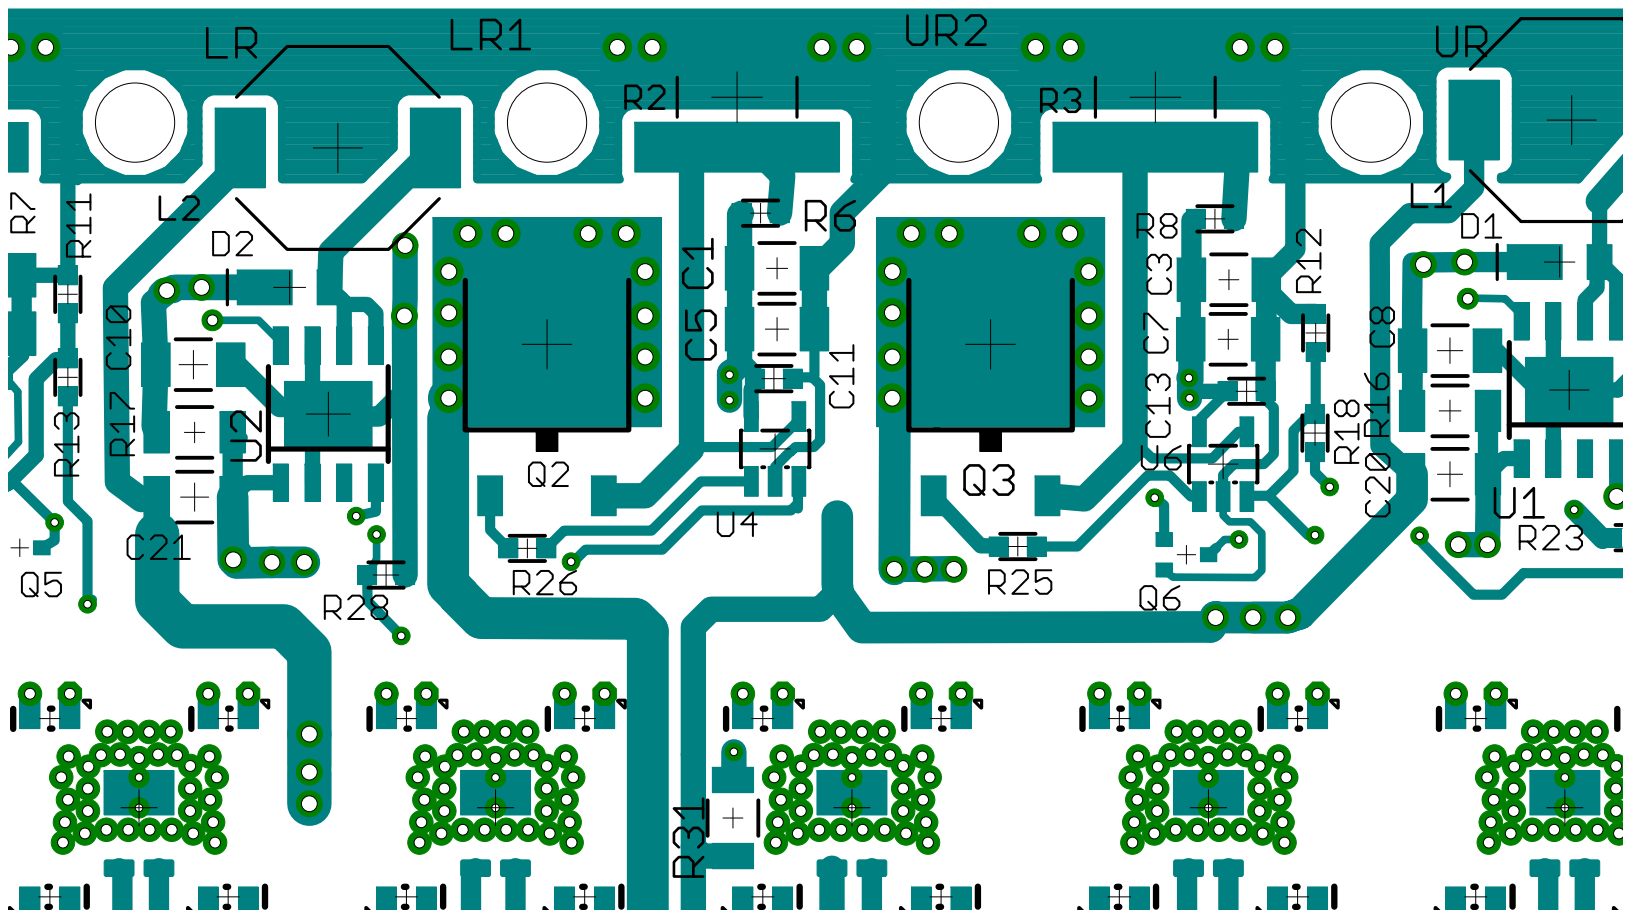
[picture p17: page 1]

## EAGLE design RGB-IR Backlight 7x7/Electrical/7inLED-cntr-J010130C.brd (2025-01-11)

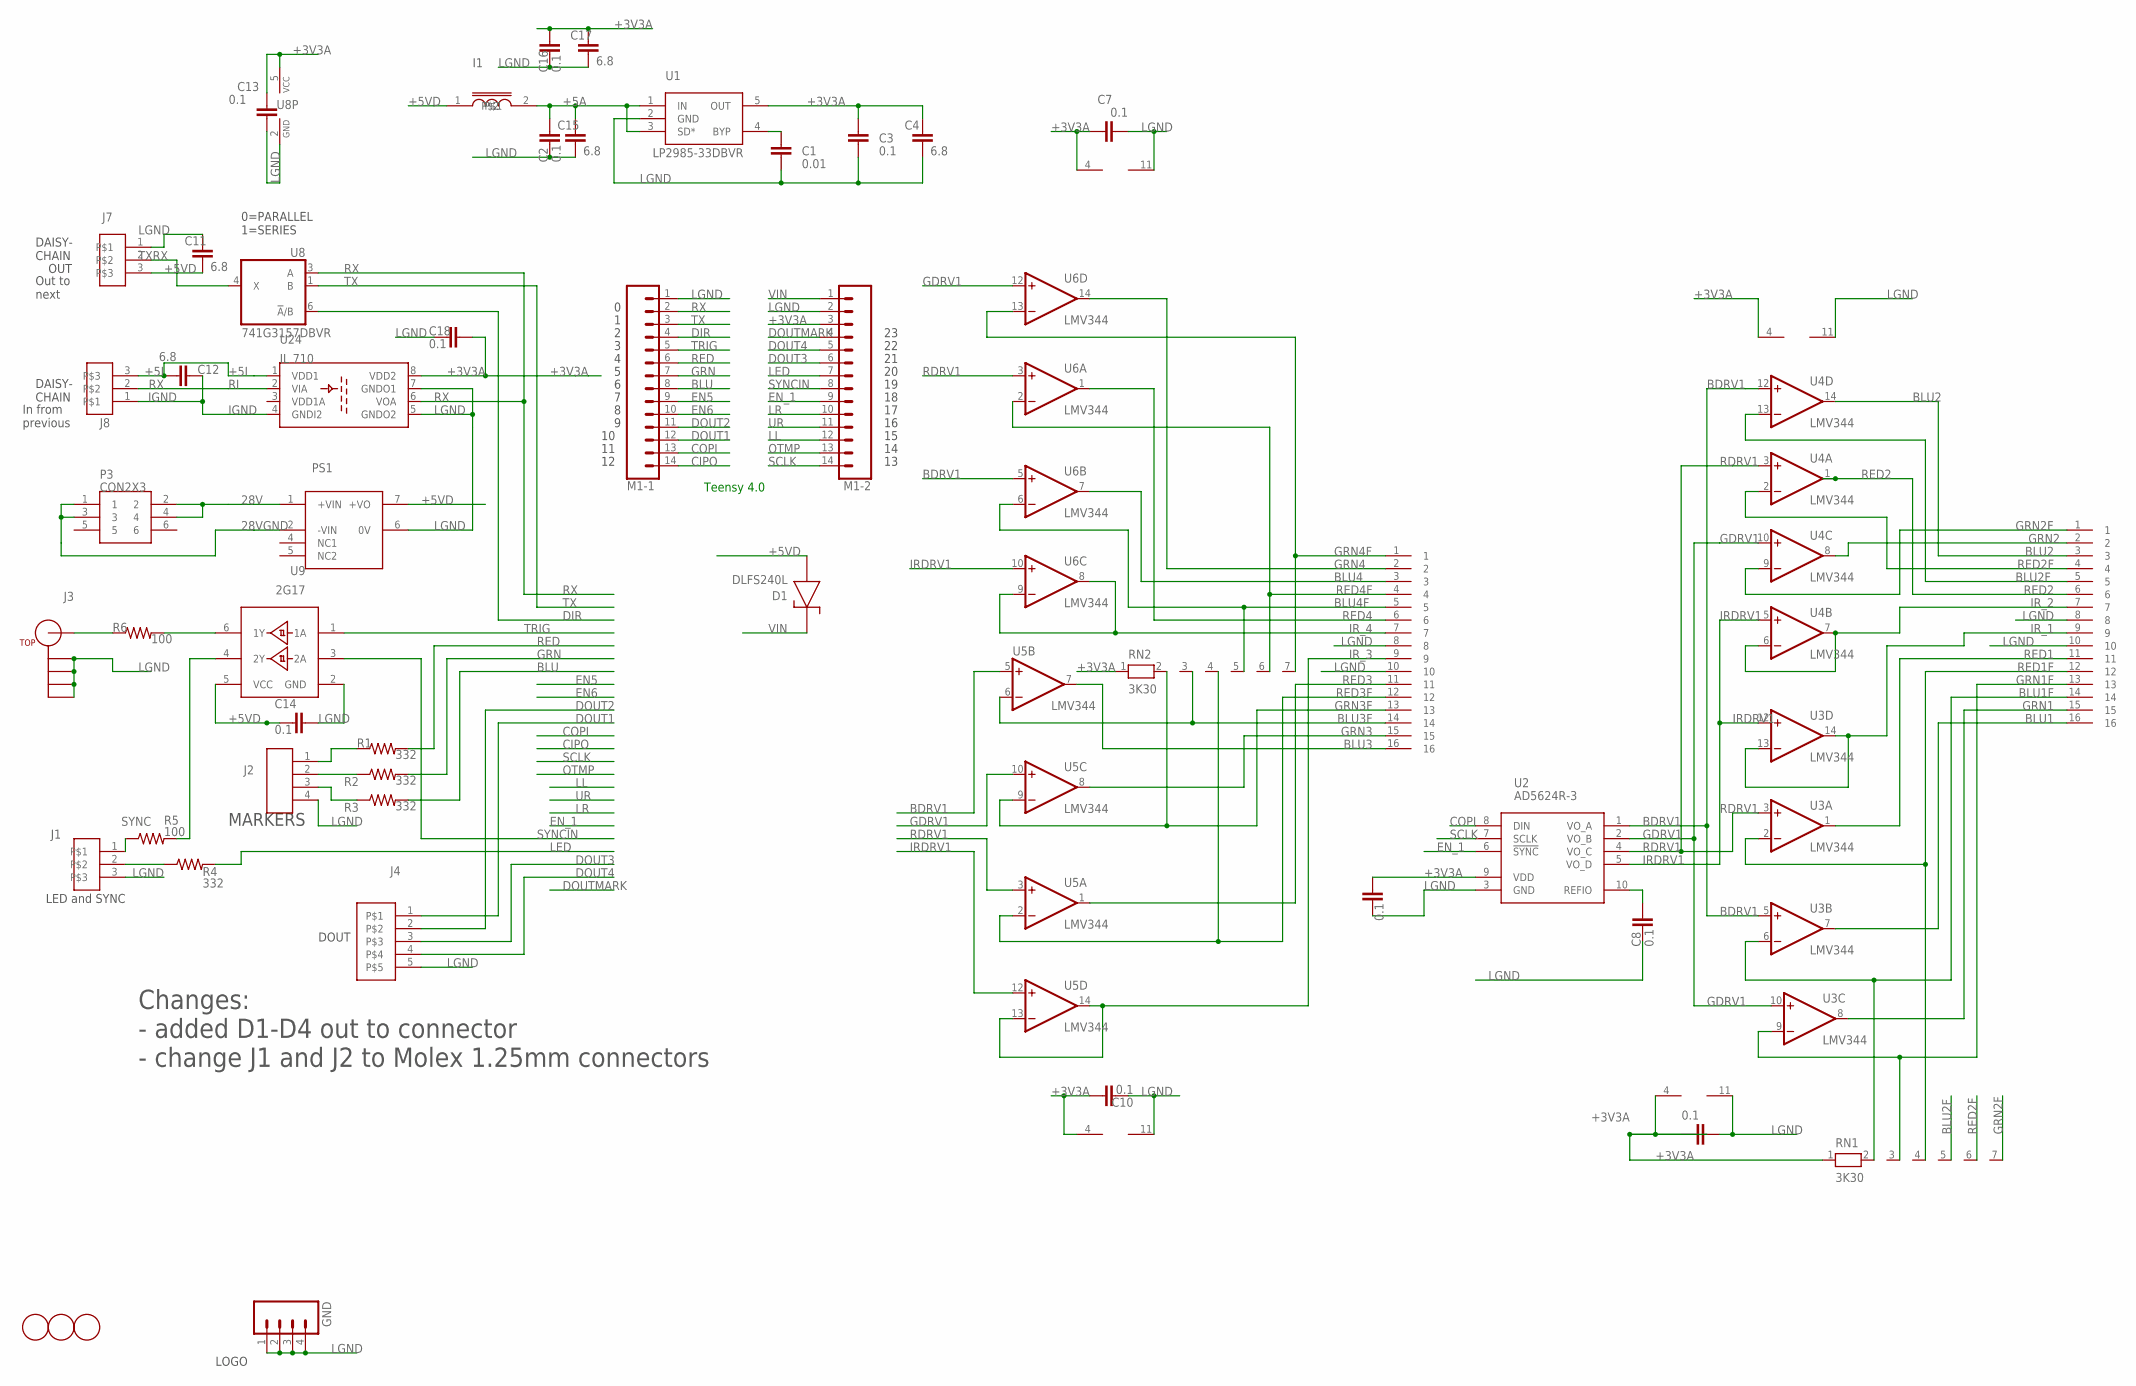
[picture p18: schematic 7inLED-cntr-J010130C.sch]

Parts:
C1: 0.01; 0805S
C2, C3, C5, C7, C8, C9, C10, C13, C14, C16, C18: 0.1; 0603S
C4, C15, C17: 6.8; 1206S
C11, C12: 6.8; 1210S
D1: DLFS240L; PWRDI-123
FID1, FID2, FID3: FIDUCIAL; FIDUCIAL_1MM
GND: M04LOCK; 1X04_LOCK
I1: INDUCTOR0805S; 0805S
J1: CON3DF13-3TH; DF13-3P-TH
J2: CON4DF13-4-TH; DF13-4-TH
J3: BNC-4PADBNC-5-1634503-1; 5-1634503-1
J4: CON5AMPMODU-5; AMPMODU-5
J7, J8: CON3AMPMODU-3; AMPMODU-3
M1-1, M1-2: CONN_14; 1X14
P1, P2: CON162X8PLUG; 2X8_PLUG
P3: CON2X3; 2X3_PLUG
PS1: DC-DCISLTDN-5W; DC-DC-TDN-5W
R1, R2, R3, R4: 332; 0805S
R5, R6: 100; 0805S
RN1, RN2: 3K30; RN-7
U1: LP2985-33DBVR; SOT23-5
U2: AD5624R-3; MSOP10
U3, U4, U5, U6: LMV344; SO14
U8: 741G3157DBVR; DBV_R-PDSO-G6
U9: 2G17; SOT23-6
U24: IL 710; MSOP08
U$2: JFRC-LOGOLOGO_OP; LOGO_BMP_OP

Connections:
28V: P3.2, P3.4, PS1.1 (+VIN)
28VGND: P3.1, P3.3, PS1.2 (-VIN)
+3V3A: C3.1, C4.1, C5.1, C7.1, C9.1, C10.1, C13.1, C16.1, C17.1, C18.1, M1-2.3, RN1.1, RN2.1, U1.5 (OUT), U2.9 (VDD), U3.4 (V+), U4.4 (V+), U5.4 (V+), U6.4 (V+), U8.5 (VCC), U24.8 (VDD2)
+5A: C2.1, C15.1, I1.2, U1.1 (IN), U1.3 (SD*)
+5I: C12.1, J8.3, U24.1 (VDD1)
+5VD: C11.2, C14.1, D1.A, I1.1, J7.3, PS1.7 (+VO), U9.5 (VCC)
BDRV1: U2.1 (VO_A), U3.5 (+IN), U4.12 (+IN), U5.5 (+IN), U6.5 (+IN)
BLU: M1-1.8, R3.2
BLU1: P1.16, U3.7 (OUT)
BLU1F: P1.14, RN1.2, U3.6 (-IN)
BLU2: P1.3, U4.14 (OUT)
BLU2F: P1.5, RN1.5, U4.13 (-IN)
BLU3: P2.16, U5.7 (OUT)
BLU3F: P2.14, RN2.3, U5.6 (-IN)
BLU4: P2.3, U6.7 (OUT)
BLU4F: P2.5, RN2.5, U6.6 (-IN)
CIPO: M1-1.14
COPI: M1-1.13, U2.8 (DIN)
DIR: M1-1.4, U8.6 (!A!/B)
DOUT1: J4.1, M1-1.12
DOUT2: J4.2, M1-1.11
DOUT3: J4.3, M1-2.6
DOUT4: J4.4, M1-2.5
DOUTMARK: M1-2.4
EN5: M1-1.9
EN6: M1-1.10
EN_1: M1-2.9, U2.6 (!SYNC)
GDRV1: U2.2 (VO_B), U3.10 (+IN), U4.10 (+IN), U5.10 (+IN), U6.12 (+IN)
GRN: M1-1.7, R2.2
GRN1: P1.15, U3.8 (OUT)
GRN1F: P1.13, RN1.3, U3.9 (-IN)
GRN2: P1.2, U4.8 (OUT)
GRN2F: P1.1, RN1.7, U4.9 (-IN)
GRN3: P2.15, U5.8 (OUT)
GRN3F: P2.13, RN2.2, U5.9 (-IN)
GRN4: P2.2, U6.14 (OUT)
GRN4F: P2.1, RN2.7, U6.13 (-IN)
IGND: C12.2, J8.1, U24.4 (GNDI2)
IRDRV1: U2.5 (VO_D), U3.12 (+IN), U4.5 (+IN), U5.12 (+IN), U6.10 (+IN)
IR_1: P1.9, U3.13 (-IN), U3.14 (OUT)
IR_2: P1.7, U4.6 (-IN), U4.7 (OUT)
IR_3: P2.9, U5.13 (-IN), U5.14 (OUT)
IR_4: P2.7, U6.8 (OUT), U6.9 (-IN)
LED: M1-2.7, R4.2
LGND: C1.2, C2.2, C3.2, C4.2, C5.2, C7.2, C8.2, C9.2, C10.2, C11.1, C13.2, C14.2, C15.2, C16.2, C17.2, C18.2, GND.1, GND.2, GND.3, GND.4, J1.3, J2.4, J3.2A (S1), J3.2B (S2), J3.2C (S3), J3.2D (S4), J4.5, J7.1, M1-1.1, M1-2.2, P1.8, P1.10, P2.8, P2.10, PS1.6 (0V), U1.2 (GND), U2.3 (GND), U3.11 (V-), U4.11 (V-), U5.11 (V-), U6.11 (V-), U8.2 (GND), U9.2 (GND), U24.5 (GNDO2), U24.7 (GNDO1)
LL: M1-2.12
LR: M1-2.10
unnamed: R6.2, U9.6 (1Y)
unnamed: R5.2, U9.4 (2Y)
unnamed: J2.3, R3.1
unnamed: C8.1, U2.10 (REFIO)
unnamed: C1.1, U1.4 (BYP)
unnamed: J2.2, R2.1
unnamed: J2.1, R1.1
unnamed: J3.1 (C), R6.1
unnamed: J1.2, R4.1
OTMP: M1-2.13
RDRV1: U2.4 (VO_C), U3.3 (+IN), U4.3 (+IN), U5.3 (+IN), U6.3 (+IN)
RED: M1-1.6, R1.2
RED1: P1.11, U3.1 (OUT)
RED1F: P1.12, RN1.4, U3.2 (-IN)
RED2: P1.6, U4.1 (OUT)
RED2F: P1.4, RN1.6, U4.2 (-IN)
RED3: P2.11, U5.1 (OUT)
RED3F: P2.12, RN2.4, U5.2 (-IN)
RED4: P2.6, U6.1 (OUT)
RED4F: P2.4, RN2.6, U6.2 (-IN)
RI: J8.2, U24.2 (VIA)
RX: M1-1.2, U8.3 (A), U24.6 (VOA)
SCLK: M1-2.14, U2.7 (SCLK)
SYNC: J1.1, R5.1
SYNCIN: M1-2.8, U9.3 (2A)
TRIG: M1-1.5, U9.1 (1A)
TX: M1-1.3, U8.1 (B)
TXRX: J7.2, U8.4 (X)
UR: M1-2.11
VIN: D1.K, M1-2.1

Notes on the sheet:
LED and SYNC
0=PARALLEL 1=SERIES
DAISY- CHAIN
In from previous
Out to next
OUT
MARKERS
Changes: - added D1-D4 out to connector - change J1 and J2 to Molex 1.25mm connectors
DOUT
Teensy 4.0

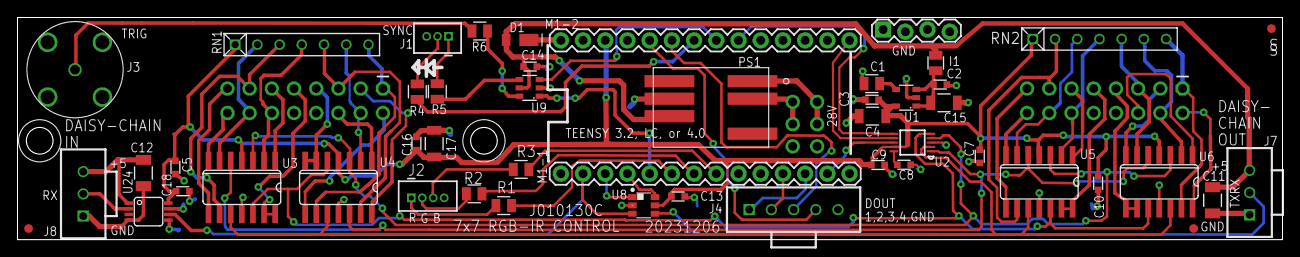
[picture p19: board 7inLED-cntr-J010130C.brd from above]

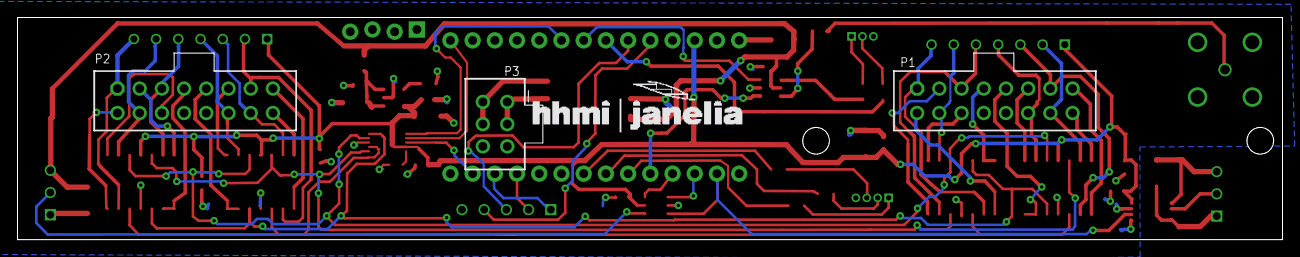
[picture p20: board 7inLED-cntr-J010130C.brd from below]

Board: 2 copper layers, 144.7 x 25.4 mm, 55 parts (4 on the bottom side), 69 nets.

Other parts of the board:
S1, S8: SCREW; 4-40SOCKET

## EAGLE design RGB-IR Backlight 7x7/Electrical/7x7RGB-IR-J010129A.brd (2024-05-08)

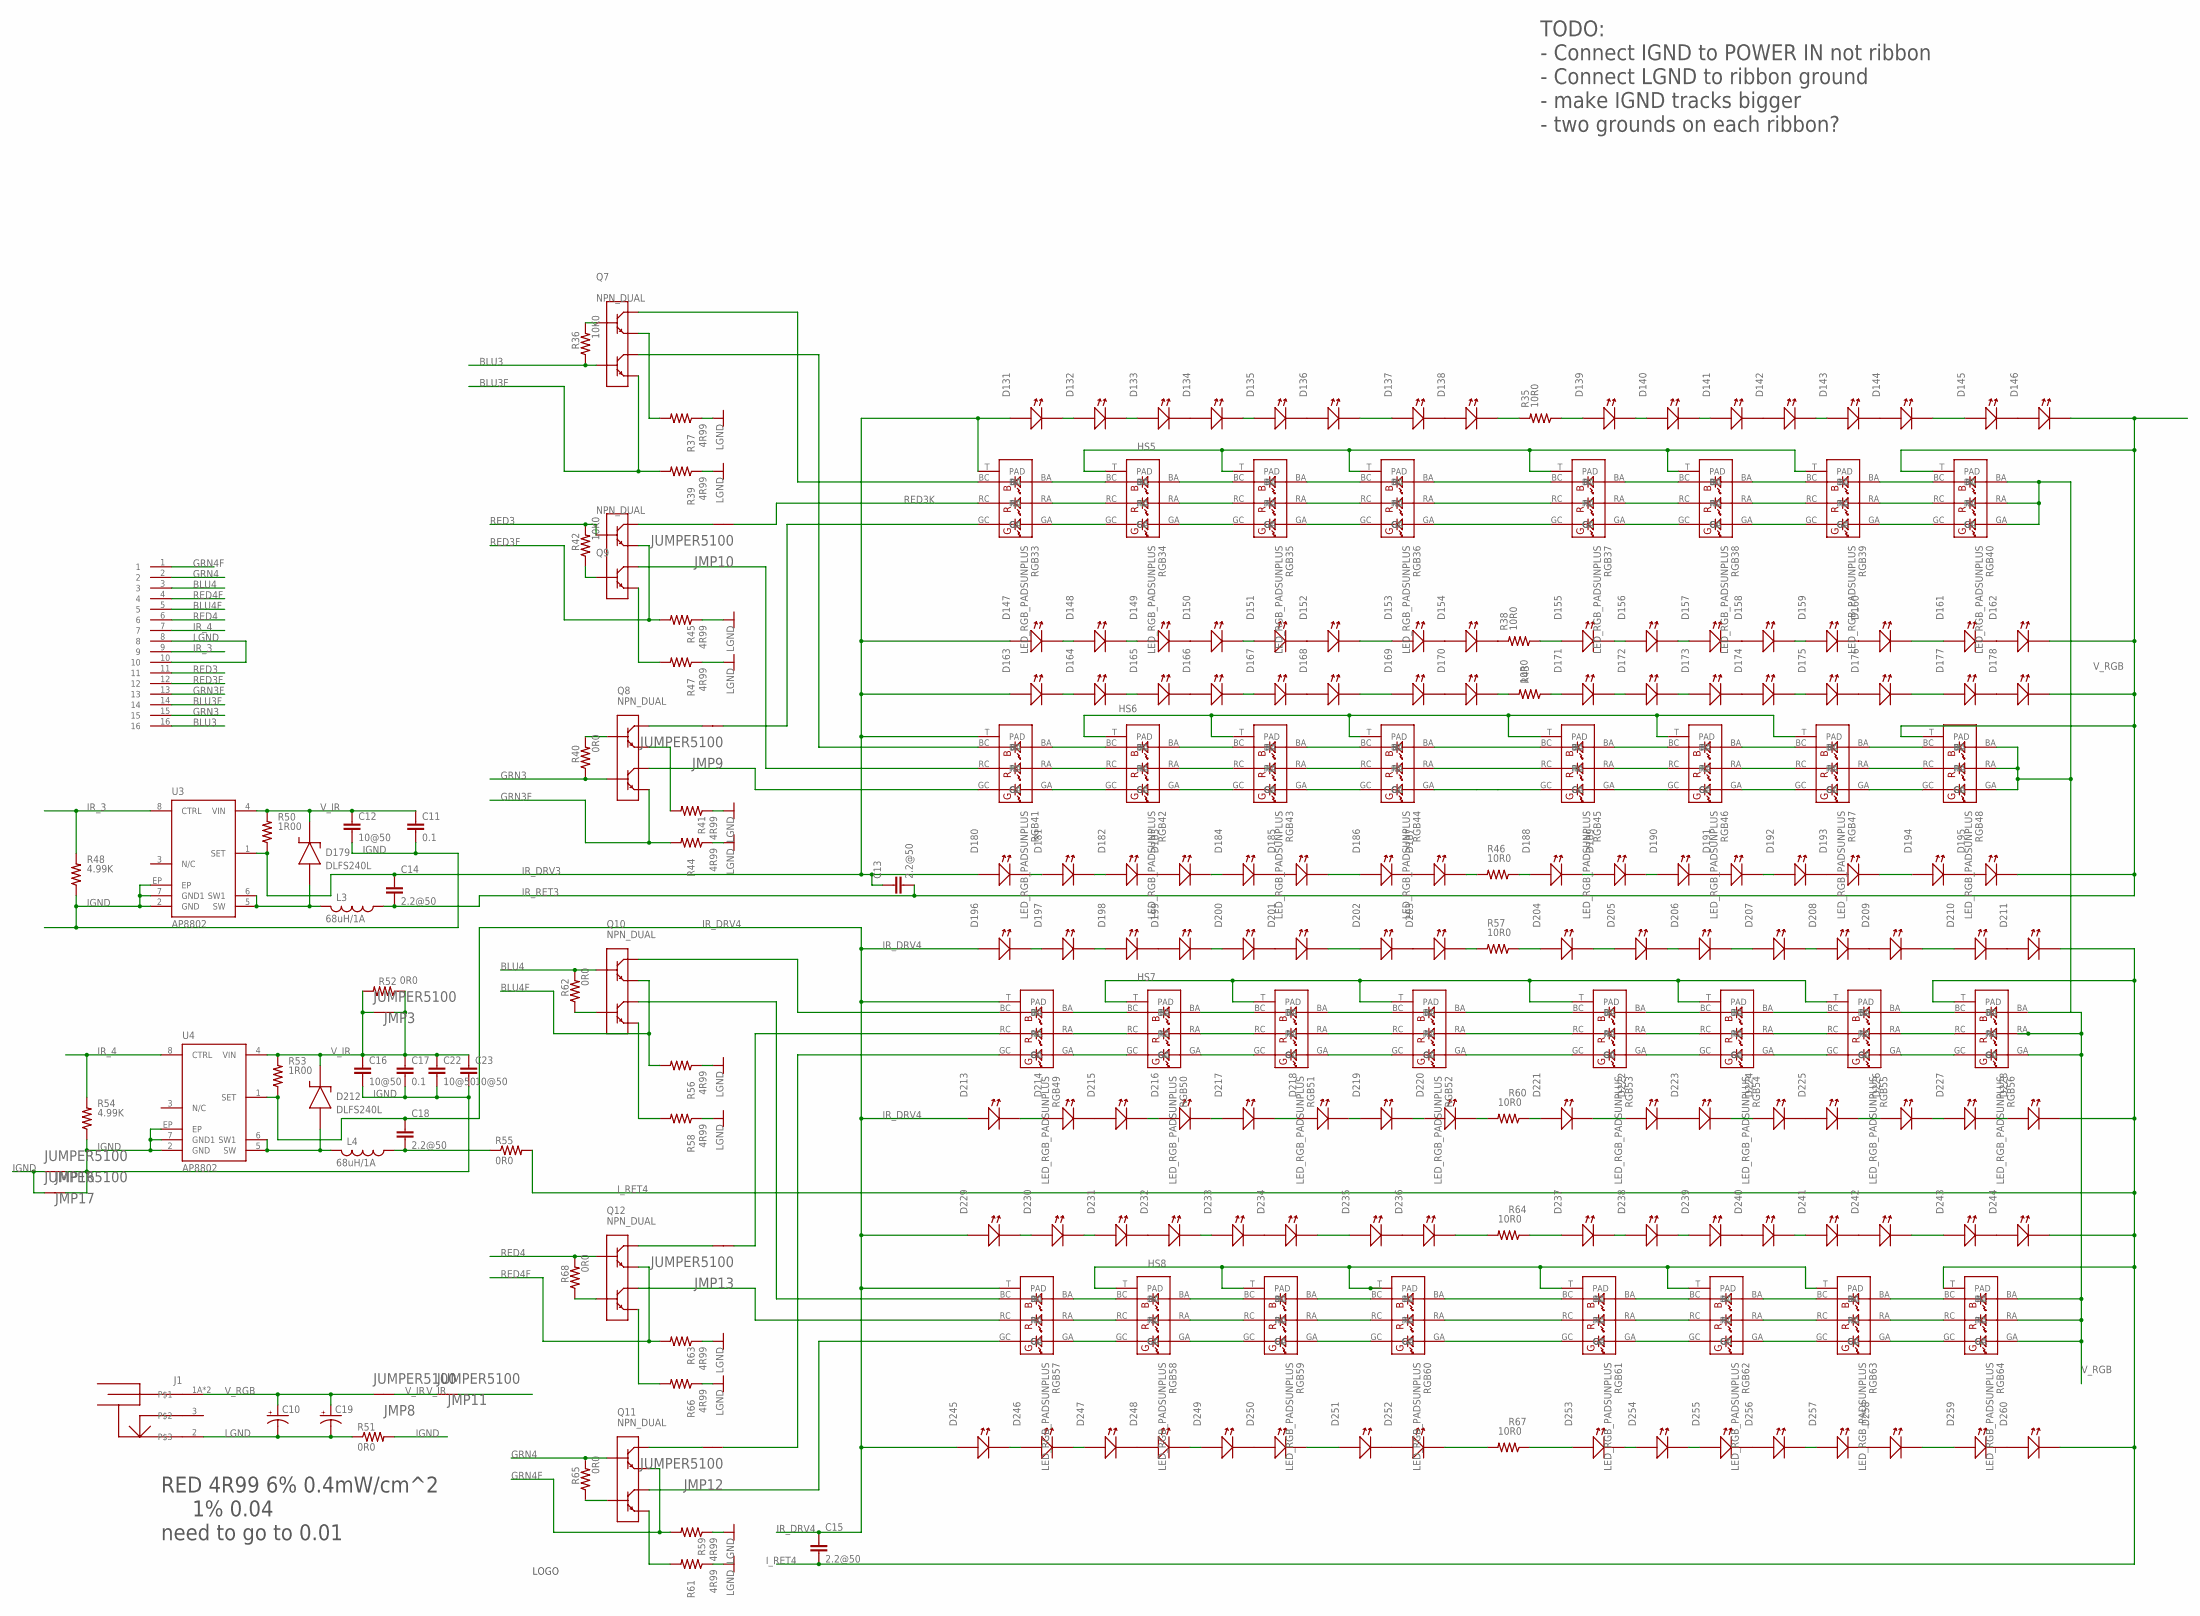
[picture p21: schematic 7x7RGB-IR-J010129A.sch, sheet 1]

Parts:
C10, C19: CPOL-US153CLV-0810; 153CLV-0810
C11, C17: 0.1; 0805S
C12, C16, C22, C23: 10@50; 1210S
C13, C14, C15, C18: 2.2@50; 1206S
D131, D132, D133, D134, D135, D136, D137, D138, D139, D140, D141, D142, D143, D144, D145, D146, D147, D148, D149, D150, D151, D152, D153, D154, D155, D156, D157, D158, D159, D160, D161, D162, D163, D164, D165, D166, D167, D168, D169, D170, D171, D172, D173, D174, D175, D176, D177, D178, D180, D181, D182, D183, D184, D185, D186, D187, D188, D189, D190, D191, D192, D193, D194, D195, D196, D197, D198, D199, D200, D201, D202, D203, D204, D205, D206, D207, D208, D209, D210, D211, D213, D214, D215, D216, D217, D218, D219, D220, D221, D222, D223, D224, D225, D226, D227, D228, D229, D230, D231, D232, D233, D234, D235, D236, D237, D238, D239, D240, D241, D242, D243, D244, D245, D246, D247, D248, D249, D250, D251, D252, D253, D254, D255, D256, D257, D258, D259, D260: LEDLED_SFH4050; LED_SFH4050
D179, D212: DLFS240L; PWRDI-123
J1: POWER_JACK_SHUNTPJ-002; PJ-002
JMP3, JMP8, JMP9, JMP10, JMP11, JMP12, JMP13, JMP16, JMP17: JUMPER5100; 5100
L3, L4: 68uH/1A; SRU8043
P2: CON162X8SM-SMALL; HEADER2X8_SM_SMALL
Q7, Q8, Q9, Q10, Q11, Q12: NPN_DUAL; LFPAK56D
R35, R38, R43, R46, R57, R60, R64, R67: 10R0; 1206S
R36, R42: 10K0; 1206S
R37, R39, R41, R44, R45, R47, R56, R58, R59, R61, R63, R66: 4R99; R2512
R40, R51, R55, R62, R65, R68: 0R0; 1206S
R48, R54: 4.99K; 0805S
R50, R53: 1R00; 1206S
R52: 0R0; R1206
RGB33, RGB34, RGB35, RGB36, RGB37, RGB38, RGB39, RGB40, RGB41, RGB42, RGB43, RGB44, RGB45, RGB46, RGB47, RGB48, RGB49, RGB50, RGB51, RGB52, RGB53, RGB54, RGB55, RGB56, RGB57, RGB58, RGB59, RGB60, RGB61, RGB62, RGB63, RGB64: LED_RGB_PADSUNPLUS; SUNPLUS_RGB
U3, U4: AP8802; SOIC8-EP
U$19: JFRC-LOGOLOGO_OP; LOGO_BMP_OP

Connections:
BLU3: P2.16, Q7.4 (B2), R36.1
BLU3F: P2.14, Q7.3 (E2), R39.2
BLU3K: Q7.7 (C1), Q7.8 (C1), Q7.78 (C1), RGB33.BC
BLU4: P2.3, Q10.2 (B1), R62.2
BLU4F: P2.5, Q10.1 (E1), R56.2
G4: Q11.3 (E2), R61.2
G4A: Q11.4 (B2), R65.1
GRN3: P2.15, Q8.4 (B2), R40.1
GRN3F: P2.13, Q8.3 (E2), R44.2
GRN3K: JMP9.1, RGB33.GC
GRN4: P2.2, Q11.2 (B1), R65.2
GRN4F: P2.1, Q11.1 (E1), R59.2
GULA_1: Q11.5 (C2), Q11.6 (C2), Q11.56 (C2), RGB57.GC
GULA_2: Q12.5 (C2), Q12.6 (C2), Q12.56 (C2), RGB57.RC
GULA_3: Q8.5 (C2), Q8.6 (C2), Q8.56 (C2), RGB41.GC
GULA_4: Q9.5 (C2), Q9.6 (C2), Q9.56 (C2), RGB41.RC
HS5: RGB34.T (PAD), RGB35.T (PAD), RGB36.T (PAD), RGB37.T (PAD), RGB38.T (PAD), RGB39.T (PAD)
HS6: RGB42.T (PAD), RGB43.T (PAD), RGB44.T (PAD), RGB45.T (PAD), RGB46.T (PAD), RGB47.T (PAD)
HS7: RGB50.T (PAD), RGB51.T (PAD), RGB52.T (PAD), RGB53.T (PAD), RGB54.T (PAD), RGB55.T (PAD)
HS8: RGB58.T (PAD), RGB59.T (PAD), RGB60.T (PAD), RGB61.T (PAD), RGB62.T (PAD), RGB63.T (PAD)
IGND: C11.2, C12.2, C16.2, C17.2, C22.2, C23.2, JMP16.1, JMP16.2, JMP17.1, JMP17.2, R48.1, R51.2, R54.1, U3.2 (GND), U3.7 (GND1), U3.EP, U4.2 (GND), U4.7 (GND1), U4.EP
IR_3: P2.9, R48.2, U3.8 (CTRL)
IR_4: P2.7, R54.2, U4.8 (CTRL)
IR_DRV3: C13.1, C14.1, D131.A, D147.A, D163.A, D180.A, R50.1, RGB33.T (PAD), RGB41.T (PAD), U3.1 (SET)
IR_DRV4: C15.1, C18.1, D196.A, D213.A, D229.A, D245.A, R53.1, RGB49.T (PAD), RGB57.T (PAD), U4.1 (SET)
IR_RET3: C13.2, C14.2, D146.C (K), D162.C (K), D178.C (K), D195.C (K), L3.1, RGB40.T (PAD), RGB48.T (PAD)
I_RET4: C15.2, D211.C (K), D228.C (K), D244.C (K), D260.C (K), R55.2, RGB56.T (PAD), RGB64.T (PAD)
LGND: C10.-, C19.-, J1.2, P2.8, P2.10, R37.1, R39.1, R41.1, R44.1, R45.1, R47.1, R51.1, R56.1, R58.1, R59.1, R61.1, R63.1, R66.1; also elsewhere on the board
unnamed: D227.C (K), D228.A
unnamed: Q12.4 (B2), R68.1
unnamed: Q8.1 (E1), R41.2
unnamed: JMP12.1, RGB49.GC
unnamed: Q10.7 (C1), Q10.8 (C1), Q10.78 (C1), RGB49.BC
unnamed: Q10.5 (C2), Q10.6 (C2), Q10.56 (C2), RGB57.BC
unnamed: Q9.3 (E2), R47.2
unnamed: Q9.4 (B2), R42.1
unnamed: Q8.2 (B1), R40.2
unnamed: D139.A, R35.1
unnamed: JMP13.2, Q12.7 (C1), Q12.8 (C1), Q12.78 (C1)
unnamed: JMP12.2, Q11.7 (C1), Q11.8 (C1), Q11.78 (C1)
unnamed: D138.C (K), R35.2
unnamed: D154.C (K), R38.2
unnamed: D155.A, R38.1
unnamed: JMP13.1, RGB49.RC
unnamed: D171.A, R43.1
unnamed: D170.C (K), R43.2
unnamed: D188.A, R46.1
unnamed: D187.C (K), R46.2
unnamed: D203.C (K), R57.2
unnamed: RGB63.BA, RGB64.BC
unnamed: D212.A, L4.2, U4.5 (SW), U4.6 (SW1)
unnamed: C18.2, L4.1, R55.1
unnamed: RGB63.RA, RGB64.RC
unnamed: D204.A, R57.1
unnamed: D221.A, R60.1
unnamed: D220.C (K), R60.2
unnamed: D237.A, R64.1
unnamed: Q10.4 (B2), R62.1
unnamed: Q10.3 (E2), R58.2
unnamed: D236.C (K), R64.2
unnamed: D253.A, R67.1
unnamed: D252.C (K), R67.2
unnamed: D179.A, L3.2, U3.5 (SW), U3.6 (SW1)
unnamed: RGB47.GA, RGB48.GC
unnamed: RGB46.GA, RGB47.GC
unnamed: RGB45.GA, RGB46.GC
unnamed: RGB44.GA, RGB45.GC
unnamed: RGB43.GA, RGB44.GC
unnamed: RGB42.GA, RGB43.GC
unnamed: RGB63.GA, RGB64.GC
unnamed: RGB41.GA, RGB42.GC
unnamed: RGB47.RA, RGB48.RC
unnamed: RGB46.RA, RGB47.RC
unnamed: RGB45.RA, RGB46.RC
unnamed: RGB44.RA, RGB45.RC
unnamed: RGB43.RA, RGB44.RC
unnamed: RGB42.RA, RGB43.RC
unnamed: RGB41.RA, RGB42.RC
unnamed: RGB41.BA, RGB42.BC
unnamed: RGB42.BA, RGB43.BC
unnamed: RGB43.BA, RGB44.BC
unnamed: RGB44.BA, RGB45.BC
unnamed: RGB45.BA, RGB46.BC
unnamed: RGB46.BA, RGB47.BC
unnamed: RGB47.BA, RGB48.BC
unnamed: D181.C (K), D182.A
unnamed: D182.C (K), D183.A
unnamed: RGB33.RA, RGB34.RC
unnamed: D184.C (K), D185.A
unnamed: D186.C (K), D187.A
unnamed: D180.C (K), D181.A
unnamed: D183.C (K), D184.A
unnamed: D185.C (K), D186.A
unnamed: D189.C (K), D190.A
unnamed: D190.C (K), D191.A
unnamed: D192.C (K), D193.A
unnamed: D194.C (K), D195.A
unnamed: D188.C (K), D189.A
unnamed: D191.C (K), D192.A
unnamed: D193.C (K), D194.A
unnamed: D164.C (K), D165.A
unnamed: D165.C (K), D166.A
unnamed: D167.C (K), D168.A
unnamed: D169.C (K), D170.A
unnamed: D163.C (K), D164.A
unnamed: D166.C (K), D167.A
unnamed: D168.C (K), D169.A
unnamed: D172.C (K), D173.A
unnamed: D173.C (K), D174.A
unnamed: D175.C (K), D176.A
unnamed: D177.C (K), D178.A
unnamed: D171.C (K), D172.A
unnamed: D174.C (K), D175.A
unnamed: D176.C (K), D177.A
unnamed: RGB55.GA, RGB56.GC
unnamed: RGB54.GA, RGB55.GC
unnamed: RGB53.GA, RGB54.GC
unnamed: RGB52.GA, RGB53.GC
unnamed: RGB51.GA, RGB52.GC
unnamed: RGB50.GA, RGB51.GC
unnamed: RGB49.GA, RGB50.GC
unnamed: RGB55.RA, RGB56.RC
unnamed: RGB54.RA, RGB55.RC
unnamed: RGB53.RA, RGB54.RC
unnamed: RGB52.RA, RGB53.RC
unnamed: RGB51.RA, RGB52.RC
unnamed: RGB50.RA, RGB51.RC
unnamed: RGB49.RA, RGB50.RC
unnamed: RGB49.BA, RGB50.BC
unnamed: RGB50.BA, RGB51.BC
unnamed: RGB51.BA, RGB52.BC
unnamed: RGB52.BA, RGB53.BC
unnamed: RGB53.BA, RGB54.BC
unnamed: RGB54.BA, RGB55.BC
unnamed: RGB55.BA, RGB56.BC
unnamed: D197.C (K), D198.A
unnamed: D198.C (K), D199.A
unnamed: D200.C (K), D201.A
unnamed: D202.C (K), D203.A
unnamed: D196.C (K), D197.A
unnamed: D199.C (K), D200.A
unnamed: D201.C (K), D202.A
unnamed: D205.C (K), D206.A
unnamed: D206.C (K), D207.A
unnamed: D208.C (K), D209.A
unnamed: D210.C (K), D211.A
unnamed: D204.C (K), D205.A
unnamed: D207.C (K), D208.A
unnamed: D209.C (K), D210.A
unnamed: D214.C (K), D215.A
unnamed: D215.C (K), D216.A
unnamed: D217.C (K), D218.A
unnamed: D219.C (K), D220.A
unnamed: D213.C (K), D214.A
unnamed: D216.C (K), D217.A
unnamed: D218.C (K), D219.A
unnamed: D222.C (K), D223.A
unnamed: D224.C (K), D225.A
unnamed: D226.C (K), D227.A
unnamed: D221.C (K), D222.A
unnamed: D223.C (K), D224.A
unnamed: D225.C (K), D226.A
unnamed: RGB39.GA, RGB40.GC
unnamed: RGB38.GA, RGB39.GC
unnamed: RGB37.GA, RGB38.GC
unnamed: RGB36.GA, RGB37.GC
unnamed: RGB35.GA, RGB36.GC
unnamed: RGB34.GA, RGB35.GC
unnamed: RGB33.GA, RGB34.GC
unnamed: RGB39.RA, RGB40.RC
unnamed: RGB38.RA, RGB39.RC
unnamed: RGB37.RA, RGB38.RC
unnamed: RGB36.RA, RGB37.RC
unnamed: RGB35.RA, RGB36.RC
unnamed: RGB34.RA, RGB35.RC
unnamed: RGB33.BA, RGB34.BC
unnamed: RGB34.BA, RGB35.BC
unnamed: RGB35.BA, RGB36.BC
unnamed: RGB36.BA, RGB37.BC
unnamed: RGB37.BA, RGB38.BC
unnamed: RGB38.BA, RGB39.BC
unnamed: RGB39.BA, RGB40.BC
unnamed: D132.C (K), D133.A
unnamed: D133.C (K), D134.A
unnamed: D135.C (K), D136.A
unnamed: D137.C (K), D138.A
unnamed: D131.C (K), D132.A
unnamed: D134.C (K), D135.A
unnamed: D136.C (K), D137.A
unnamed: D140.C (K), D141.A
unnamed: D141.C (K), D142.A
unnamed: D143.C (K), D144.A
unnamed: D145.C (K), D146.A
unnamed: D139.C (K), D140.A
unnamed: D142.C (K), D143.A
unnamed: D144.C (K), D145.A
unnamed: D148.C (K), D149.A
unnamed: D149.C (K), D150.A
unnamed: D151.C (K), D152.A
unnamed: D153.C (K), D154.A
unnamed: D147.C (K), D148.A
unnamed: D150.C (K), D151.A
unnamed: D152.C (K), D153.A
unnamed: D156.C (K), D157.A
unnamed: D157.C (K), D158.A
unnamed: D159.C (K), D160.A
unnamed: D161.C (K), D162.A
unnamed: D155.C (K), D156.A
unnamed: D158.C (K), D159.A
unnamed: D160.C (K), D161.A
unnamed: Q7.1 (E1), R37.2
unnamed: Q7.5 (C2), Q7.6 (C2), Q7.56 (C2), RGB41.BC
unnamed: RGB62.GA, RGB63.GC
unnamed: RGB61.GA, RGB62.GC
unnamed: RGB60.GA, RGB61.GC
unnamed: RGB59.GA, RGB60.GC
unnamed: RGB58.GA, RGB59.GC
unnamed: RGB57.GA, RGB58.GC
unnamed: RGB62.RA, RGB63.RC
unnamed: RGB61.RA, RGB62.RC
unnamed: RGB60.RA, RGB61.RC
unnamed: RGB59.RA, RGB60.RC
unnamed: RGB58.RA, RGB59.RC
unnamed: RGB57.RA, RGB58.RC
unnamed: RGB57.BA, RGB58.BC
unnamed: RGB58.BA, RGB59.BC
unnamed: RGB59.BA, RGB60.BC
unnamed: RGB60.BA, RGB61.BC
unnamed: RGB61.BA, RGB62.BC
unnamed: RGB62.BA, RGB63.BC
unnamed: D230.C (K), D231.A
unnamed: D231.C (K), D232.A
unnamed: D233.C (K), D234.A
unnamed: D235.C (K), D236.A
unnamed: D229.C (K), D230.A
unnamed: D232.C (K), D233.A
unnamed: D234.C (K), D235.A
unnamed: D238.C (K), D239.A
unnamed: D239.C (K), D240.A
unnamed: D241.C (K), D242.A
unnamed: D243.C (K), D244.A
unnamed: D237.C (K), D238.A
unnamed: D240.C (K), D241.A
unnamed: D242.C (K), D243.A
unnamed: D246.C (K), D247.A
unnamed: D247.C (K), D248.A
unnamed: D249.C (K), D250.A
unnamed: D251.C (K), D252.A
unnamed: D245.C (K), D246.A
unnamed: D248.C (K), D249.A
unnamed: D250.C (K), D251.A
unnamed: D254.C (K), D255.A
unnamed: D255.C (K), D256.A
unnamed: D257.C (K), D258.A
unnamed: D259.C (K), D260.A
unnamed: D253.C (K), D254.A
unnamed: D256.C (K), D257.A
unnamed: D258.C (K), D259.A
unnamed: JMP10.2, Q9.7 (C1), Q9.8 (C1), Q9.78 (C1)
unnamed: JMP9.2, Q8.7 (C1), Q8.8 (C1), Q8.78 (C1)
unnamed: Q7.2 (B1), R36.2
R4: Q12.3 (E2), R66.2
RED3: P2.11, Q9.2 (B1), R42.2
RED3F: P2.12, Q9.1 (E1), R45.2
RED3K: JMP10.1, RGB33.RC
RED4: P2.6, Q12.2 (B1), R68.2
RED4F: P2.4, Q12.1 (E1), R63.2
V_IR: C11.1, C12.1, C16.1, C17.1, C22.1, C23.1, D179.K, D212.K, JMP3.1, JMP3.2, JMP8.2, JMP11.1, JMP11.2, R50.2, R52.1, R52.2, R53.2, U3.4 (VIN), U4.4 (VIN)
V_RGB: C10.+, C19.+, J1.1A, J1.1B, JMP8.1, RGB40.BA, RGB40.GA, RGB40.RA, RGB48.BA, RGB48.GA, RGB48.RA, RGB56.BA, RGB56.GA, RGB56.RA, RGB64.BA, RGB64.GA, RGB64.RA; also elsewhere on the board

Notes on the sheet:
RED 4R99 6% 0.4mW/cm^2 1% 0.04 need to go to 0.01
TODO: - Connect IGND to POWER IN not ribbon - Connect LGND to ribbon ground - make IGND tracks bigger - two grounds on each ribbon?

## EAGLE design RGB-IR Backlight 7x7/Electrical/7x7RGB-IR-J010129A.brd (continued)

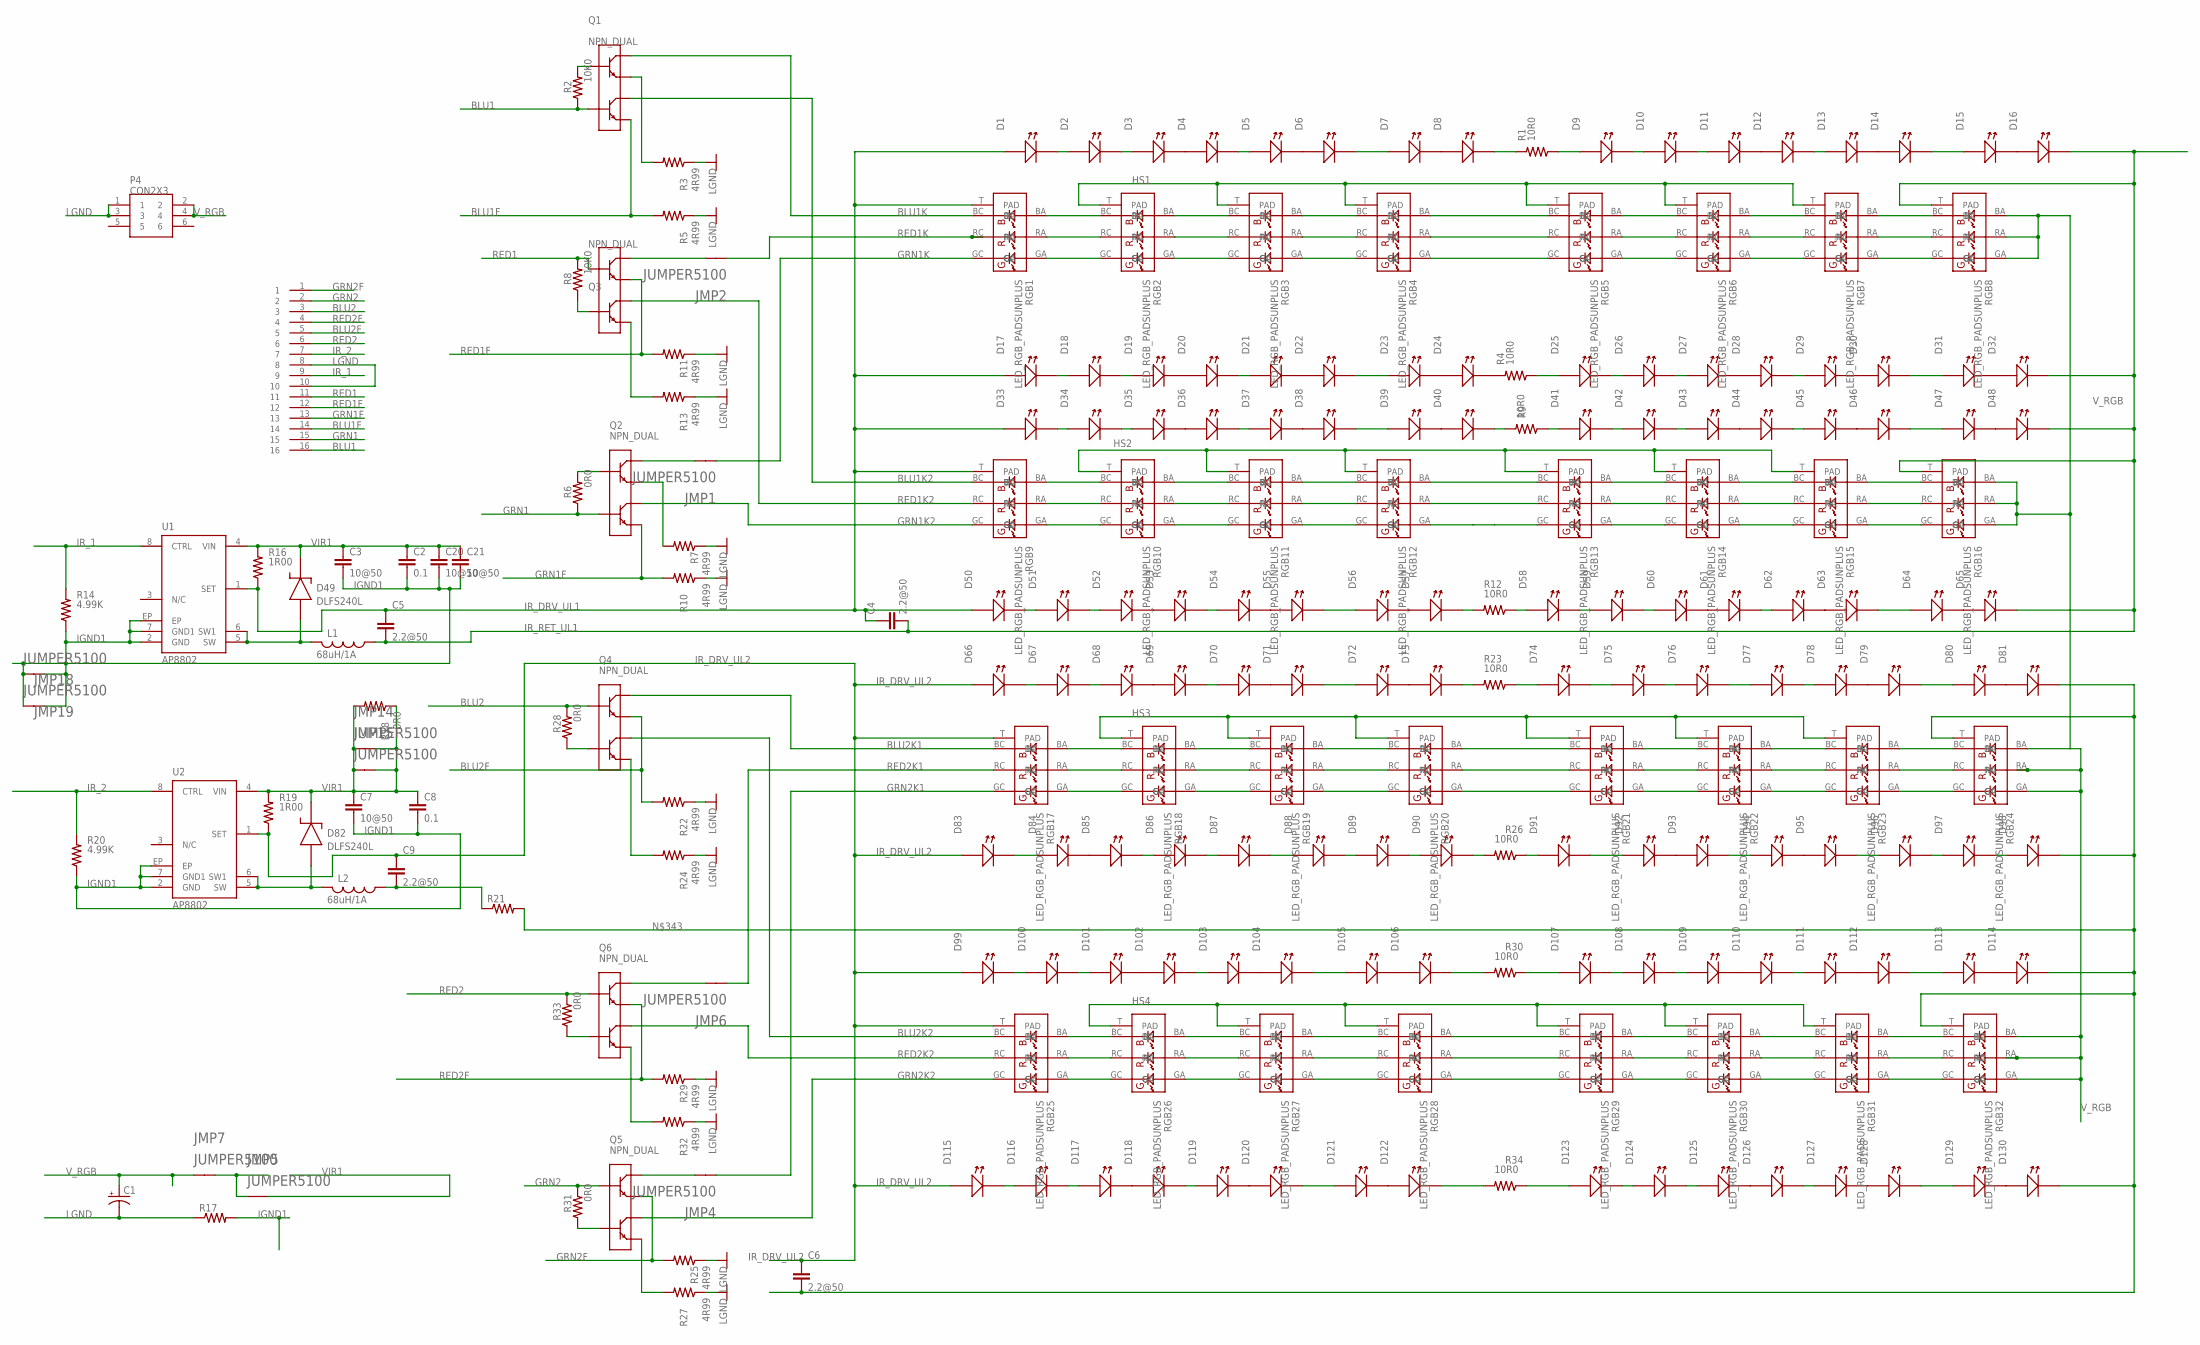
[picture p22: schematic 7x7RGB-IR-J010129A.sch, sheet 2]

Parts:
C1: CPOL-US153CLV-0810; 153CLV-0810
C2, C8: 0.1; 0805S
C3, C7, C20, C21: 10@50; 1210S
C4, C5, C6, C9: 2.2@50; 1206S
D1, D2, D3, D4, D5, D6, D7, D8, D9, D10, D11, D12, D13, D14, D15, D16, D17, D18, D19, D20, D21, D22, D23, D24, D25, D26, D27, D28, D29, D30, D31, D32, D33, D34, D35, D36, D37, D38, D39, D40, D41, D42, D43, D44, D45, D46, D47, D48, D50, D51, D52, D53, D54, D55, D56, D57, D58, D59, D60, D61, D62, D63, D64, D65, D66, D67, D68, D69, D70, D71, D72, D73, D74, D75, D76, D77, D78, D79, D80, D81, D83, D84, D85, D86, D87, D88, D89, D90, D91, D92, D93, D94, D95, D96, D97, D98, D99, D100, D101, D102, D103, D104, D105, D106, D107, D108, D109, D110, D111, D112, D113, D114, D115, D116, D117, D118, D119, D120, D121, D122, D123, D124, D125, D126, D127, D128, D129, D130: LEDLED_SFH4050; LED_SFH4050
D49, D82: DLFS240L; PWRDI-123
JMP1, JMP2, JMP4, JMP5, JMP6, JMP7, JMP14, JMP15, JMP18, JMP19: JUMPER5100; 5100
L1, L2: 68uH/1A; SRU8043
P1: CON162X8SM-SMALL; HEADER2X8_SM_SMALL
P4: CON2X3; 2X3_SHROUDED_SMT
Q1, Q2, Q3, Q4, Q5, Q6: NPN_DUAL; LFPAK56D
R1, R4, R9, R12, R23, R26, R30, R34: 10R0; 1206S
R2, R8: 10K0; 1206S
R3, R5, R7, R10, R11, R13, R22, R24, R25, R27, R29, R32: 4R99; R2512
R6, R28, R31, R33: 0R0; 1206S
R14, R20: 4.99K; 0805S
R16, R19: 1R00; 1206S
R17, R21: RESISTOR_SM1206S; 1206S
R18: 0R0; R1206
RGB1, RGB2, RGB3, RGB4, RGB5, RGB6, RGB7, RGB8, RGB9, RGB10, RGB11, RGB12, RGB13, RGB14, RGB15, RGB16, RGB17, RGB18, RGB19, RGB20, RGB21, RGB22, RGB23, RGB24, RGB25, RGB26, RGB27, RGB28, RGB29, RGB30, RGB31, RGB32: LED_RGB_PADSUNPLUS; SUNPLUS_RGB
U1, U2: AP8802; SOIC8-EP

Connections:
BLU1: P1.16, Q1.4 (B2), R2.1
BLU1F: P1.14, Q1.3 (E2), R5.2
BLU1K: Q1.7 (C1), Q1.8 (C1), Q1.78 (C1), RGB1.BC
BLU1K2: Q1.5 (C2), Q1.6 (C2), Q1.56 (C2), RGB9.BC
BLU2: P1.3, Q4.2 (B1), R28.2
BLU2F: P1.5, Q4.1 (E1), R22.2
BLU2K1: Q4.7 (C1), Q4.8 (C1), Q4.78 (C1), RGB17.BC
BLU2K2: Q4.5 (C2), Q4.6 (C2), Q4.56 (C2), RGB25.BC
G1: Q5.3 (E2), R27.2
G4A1: Q5.4 (B2), R31.1
GRN1: P1.15, Q2.4 (B2), R6.1
GRN1F: P1.13, Q2.3 (E2), R10.2
GRN1K: JMP1.1, RGB1.GC
GRN1K2: Q2.5 (C2), Q2.6 (C2), Q2.56 (C2), RGB9.GC
GRN2: P1.2, Q5.2 (B1), R31.2
GRN2F: P1.1, Q5.1 (E1), R25.2
GRN2K1: JMP4.1, RGB17.GC
GRN2K2: Q5.5 (C2), Q5.6 (C2), Q5.56 (C2), RGB25.GC
HS1: RGB2.T (PAD), RGB3.T (PAD), RGB4.T (PAD), RGB5.T (PAD), RGB6.T (PAD), RGB7.T (PAD)
HS2: RGB10.T (PAD), RGB11.T (PAD), RGB12.T (PAD), RGB13.T (PAD), RGB14.T (PAD), RGB15.T (PAD)
HS3: RGB18.T (PAD), RGB19.T (PAD), RGB20.T (PAD), RGB21.T (PAD), RGB22.T (PAD), RGB23.T (PAD)
HS4: RGB26.T (PAD), RGB27.T (PAD), RGB28.T (PAD), RGB29.T (PAD), RGB30.T (PAD), RGB31.T (PAD)
IGND1: C2.2, C3.2, C7.2, C8.2, C20.2, C21.2, JMP18.1, JMP18.2, JMP19.1, JMP19.2, R14.1, R17.2, R20.1, U1.2 (GND), U1.7 (GND1), U1.EP, U2.2 (GND), U2.7 (GND1), U2.EP
IR_1: P1.9, R14.2, U1.8 (CTRL)
IR_2: P1.7, R20.2, U2.8 (CTRL)
IR_DRV_UL1: C4.1, C5.1, D1.A, D17.A, D33.A, D50.A, R16.1, RGB1.T (PAD), RGB9.T (PAD), U1.1 (SET)
IR_DRV_UL2: C6.1, C9.1, D66.A, D83.A, D99.A, D115.A, R19.1, RGB17.T (PAD), RGB25.T (PAD), U2.1 (SET)
IR_RET_UL1: C4.2, C5.2, D16.C (K), D32.C (K), D48.C (K), D65.C (K), L1.1, RGB8.T (PAD), RGB16.T (PAD)
LGND: C1.-, P1.8, P1.10, P4.1, P4.3, R3.1, R5.1, R7.1, R10.1, R11.1, R13.1, R17.1, R22.1, R24.1, R25.1, R27.1, R29.1, R32.1; also elsewhere on the board
unnamed: RGB15.GA, RGB16.GC
unnamed: RGB14.GA, RGB15.GC
unnamed: RGB13.GA, RGB14.GC
unnamed: RGB12.GA, RGB13.GC
unnamed: RGB11.GA, RGB12.GC
unnamed: RGB10.GA, RGB11.GC
unnamed: RGB9.GA, RGB10.GC
unnamed: RGB15.RA, RGB16.RC
unnamed: RGB14.RA, RGB15.RC
unnamed: RGB13.RA, RGB14.RC
unnamed: RGB12.RA, RGB13.RC
unnamed: RGB11.RA, RGB12.RC
unnamed: RGB10.RA, RGB11.RC
unnamed: RGB9.RA, RGB10.RC
unnamed: RGB9.BA, RGB10.BC
unnamed: RGB10.BA, RGB11.BC
unnamed: RGB11.BA, RGB12.BC
unnamed: RGB12.BA, RGB13.BC
unnamed: RGB13.BA, RGB14.BC
unnamed: RGB14.BA, RGB15.BC
unnamed: RGB15.BA, RGB16.BC
unnamed: D51.C (K), D52.A
unnamed: D52.C (K), D53.A
unnamed: D54.C (K), D55.A
unnamed: D56.C (K), D57.A
unnamed: D50.C (K), D51.A
unnamed: D53.C (K), D54.A
unnamed: D55.C (K), D56.A
unnamed: D59.C (K), D60.A
unnamed: D60.C (K), D61.A
unnamed: D62.C (K), D63.A
unnamed: D64.C (K), D65.A
unnamed: D58.C (K), D59.A
unnamed: D61.C (K), D62.A
unnamed: D63.C (K), D64.A
unnamed: D34.C (K), D35.A
unnamed: D35.C (K), D36.A
unnamed: D37.C (K), D38.A
unnamed: D39.C (K), D40.A
unnamed: D33.C (K), D34.A
unnamed: D36.C (K), D37.A
unnamed: D38.C (K), D39.A
unnamed: D42.C (K), D43.A
unnamed: D43.C (K), D44.A
unnamed: D45.C (K), D46.A
unnamed: D47.C (K), D48.A
unnamed: D41.C (K), D42.A
unnamed: D44.C (K), D45.A
unnamed: D46.C (K), D47.A
unnamed: RGB23.GA, RGB24.GC
unnamed: RGB22.GA, RGB23.GC
unnamed: RGB21.GA, RGB22.GC
unnamed: RGB20.GA, RGB21.GC
unnamed: RGB19.GA, RGB20.GC
unnamed: RGB18.GA, RGB19.GC
unnamed: RGB17.GA, RGB18.GC
unnamed: RGB23.RA, RGB24.RC
unnamed: RGB22.RA, RGB23.RC
unnamed: RGB21.RA, RGB22.RC
unnamed: RGB20.RA, RGB21.RC
unnamed: RGB19.RA, RGB20.RC
unnamed: RGB18.RA, RGB19.RC
unnamed: RGB17.RA, RGB18.RC
unnamed: RGB17.BA, RGB18.BC
unnamed: RGB18.BA, RGB19.BC
unnamed: RGB19.BA, RGB20.BC
unnamed: RGB20.BA, RGB21.BC
unnamed: RGB21.BA, RGB22.BC
unnamed: RGB22.BA, RGB23.BC
unnamed: RGB23.BA, RGB24.BC
unnamed: D67.C (K), D68.A
unnamed: D68.C (K), D69.A
unnamed: D70.C (K), D71.A
unnamed: D72.C (K), D73.A
unnamed: D66.C (K), D67.A
unnamed: D69.C (K), D70.A
unnamed: D71.C (K), D72.A
unnamed: D75.C (K), D76.A
unnamed: D76.C (K), D77.A
unnamed: D78.C (K), D79.A
unnamed: D80.C (K), D81.A
unnamed: D74.C (K), D75.A
unnamed: D77.C (K), D78.A
unnamed: D79.C (K), D80.A
unnamed: D84.C (K), D85.A
unnamed: D85.C (K), D86.A
unnamed: D87.C (K), D88.A
unnamed: D89.C (K), D90.A
unnamed: D83.C (K), D84.A
unnamed: D86.C (K), D87.A
unnamed: D88.C (K), D89.A
unnamed: D92.C (K), D93.A
unnamed: D94.C (K), D95.A
unnamed: D96.C (K), D97.A
unnamed: D91.C (K), D92.A
unnamed: D93.C (K), D94.A
unnamed: D95.C (K), D96.A
unnamed: RGB7.GA, RGB8.GC
unnamed: RGB6.GA, RGB7.GC
unnamed: RGB5.GA, RGB6.GC
unnamed: RGB4.GA, RGB5.GC
unnamed: RGB3.GA, RGB4.GC
unnamed: RGB2.GA, RGB3.GC
unnamed: RGB1.GA, RGB2.GC
unnamed: RGB7.RA, RGB8.RC
unnamed: RGB6.RA, RGB7.RC
unnamed: RGB5.RA, RGB6.RC
unnamed: RGB4.RA, RGB5.RC
unnamed: RGB3.RA, RGB4.RC
unnamed: RGB2.RA, RGB3.RC
unnamed: RGB1.RA, RGB2.RC
unnamed: RGB1.BA, RGB2.BC
unnamed: RGB2.BA, RGB3.BC
unnamed: RGB3.BA, RGB4.BC
unnamed: RGB4.BA, RGB5.BC
unnamed: RGB5.BA, RGB6.BC
unnamed: RGB6.BA, RGB7.BC
unnamed: RGB7.BA, RGB8.BC
unnamed: D2.C (K), D3.A
unnamed: D3.C (K), D4.A
unnamed: D5.C (K), D6.A
unnamed: D7.C (K), D8.A
unnamed: D1.C (K), D2.A
unnamed: D4.C (K), D5.A
unnamed: D6.C (K), D7.A
unnamed: D10.C (K), D11.A
unnamed: D11.C (K), D12.A
unnamed: D13.C (K), D14.A
unnamed: D15.C (K), D16.A
unnamed: D9.C (K), D10.A
unnamed: D12.C (K), D13.A
unnamed: D14.C (K), D15.A
unnamed: D18.C (K), D19.A
unnamed: D19.C (K), D20.A
unnamed: D21.C (K), D22.A
unnamed: D23.C (K), D24.A
unnamed: D17.C (K), D18.A
unnamed: D20.C (K), D21.A
unnamed: D22.C (K), D23.A
unnamed: D26.C (K), D27.A
unnamed: D27.C (K), D28.A
unnamed: D29.C (K), D30.A
unnamed: D31.C (K), D32.A
unnamed: D25.C (K), D26.A
unnamed: D28.C (K), D29.A
unnamed: D30.C (K), D31.A
unnamed: Q1.1 (E1), R3.2
unnamed: RGB31.GA, RGB32.GC
unnamed: RGB30.GA, RGB31.GC
unnamed: RGB29.GA, RGB30.GC
unnamed: RGB28.GA, RGB29.GC
unnamed: RGB27.GA, RGB28.GC
unnamed: RGB26.GA, RGB27.GC
unnamed: RGB25.GA, RGB26.GC
unnamed: RGB31.RA, RGB32.RC
unnamed: RGB30.RA, RGB31.RC
unnamed: RGB29.RA, RGB30.RC
unnamed: RGB28.RA, RGB29.RC
unnamed: RGB27.RA, RGB28.RC
unnamed: RGB26.RA, RGB27.RC
unnamed: RGB25.RA, RGB26.RC
unnamed: RGB25.BA, RGB26.BC
unnamed: RGB26.BA, RGB27.BC
unnamed: RGB27.BA, RGB28.BC
unnamed: RGB28.BA, RGB29.BC
unnamed: RGB29.BA, RGB30.BC
unnamed: RGB30.BA, RGB31.BC
unnamed: RGB31.BA, RGB32.BC
unnamed: D100.C (K), D101.A
unnamed: D101.C (K), D102.A
unnamed: D103.C (K), D104.A
unnamed: D105.C (K), D106.A
unnamed: D99.C (K), D100.A
unnamed: D102.C (K), D103.A
unnamed: D104.C (K), D105.A
unnamed: D108.C (K), D109.A
unnamed: D109.C (K), D110.A
unnamed: D111.C (K), D112.A
unnamed: D113.C (K), D114.A
unnamed: D107.C (K), D108.A
unnamed: D110.C (K), D111.A
unnamed: D112.C (K), D113.A
unnamed: D116.C (K), D117.A
unnamed: D117.C (K), D118.A
unnamed: D119.C (K), D120.A
unnamed: D121.C (K), D122.A
unnamed: D115.C (K), D116.A
unnamed: D118.C (K), D119.A
unnamed: D120.C (K), D121.A
unnamed: D124.C (K), D125.A
unnamed: D125.C (K), D126.A
unnamed: D127.C (K), D128.A
unnamed: D129.C (K), D130.A
unnamed: D123.C (K), D124.A
unnamed: D126.C (K), D127.A
unnamed: D128.C (K), D129.A
unnamed: JMP2.2, Q3.7 (C1), Q3.8 (C1), Q3.78 (C1)
unnamed: JMP1.2, Q2.7 (C1), Q2.8 (C1), Q2.78 (C1)
unnamed: Q1.2 (B1), R2.2
unnamed: D97.C (K), D98.A
unnamed: JMP6.2, Q6.7 (C1), Q6.8 (C1), Q6.78 (C1)
unnamed: JMP4.2, Q5.7 (C1), Q5.8 (C1), Q5.78 (C1)
unnamed: D49.A, L1.2, U1.5 (SW), U1.6 (SW1)
unnamed: D82.A, L2.2, U2.5 (SW), U2.6 (SW1)
unnamed: C6.2, D81.C (K), D98.C (K), D114.C (K), D130.C (K), R21.2, RGB24.T (PAD), RGB32.T (PAD)
unnamed: C9.2, L2.1, R21.1
unnamed: JMP5.1, JMP7.2
unnamed: Q6.4 (B2), R33.1
unnamed: Q4.4 (B2), R28.1
unnamed: Q4.3 (E2), R24.2
unnamed: Q3.3 (E2), R13.2
unnamed: Q3.4 (B2), R8.1
unnamed: Q2.1 (E1), R7.2
unnamed: Q2.2 (B1), R6.2
unnamed: D9.A, R1.1
unnamed: D8.C (K), R1.2
unnamed: D24.C (K), R4.2
unnamed: D25.A, R4.1
unnamed: D41.A, R9.1
unnamed: D40.C (K), R9.2
unnamed: D58.A, R12.1
unnamed: D57.C (K), R12.2
unnamed: D73.C (K), R23.2
unnamed: D74.A, R23.1
unnamed: D91.A, R26.1
unnamed: D90.C (K), R26.2
unnamed: D107.A, R30.1
unnamed: D106.C (K), R30.2
unnamed: D123.A, R34.1
unnamed: D122.C (K), R34.2
R1: Q6.3 (E2), R32.2
RED1: P1.11, Q3.2 (B1), R8.2
RED1F: P1.12, Q3.1 (E1), R11.2
RED1K: JMP2.1, RGB1.RC
RED1K2: Q3.5 (C2), Q3.6 (C2), Q3.56 (C2), RGB9.RC
RED2: P1.6, Q6.2 (B1), R33.2
RED2F: P1.4, Q6.1 (E1), R29.2
RED2K1: JMP6.1, RGB17.RC
RED2K2: Q6.5 (C2), Q6.6 (C2), Q6.56 (C2), RGB25.RC
VIR1: C2.1, C3.1, C7.1, C8.1, C20.1, C21.1, D49.K, D82.K, JMP5.2, JMP14.1, JMP14.2, JMP15.1, JMP15.2, R16.2, R18.1, R18.2, R19.2, U1.4 (VIN), U2.4 (VIN)
V_RGB: C1.+, JMP7.1, P4.2, P4.4, RGB8.BA, RGB8.GA, RGB8.RA, RGB16.BA, RGB16.GA, RGB16.RA, RGB24.BA, RGB24.GA, RGB24.RA, RGB32.BA, RGB32.GA, RGB32.RA; also elsewhere on the board

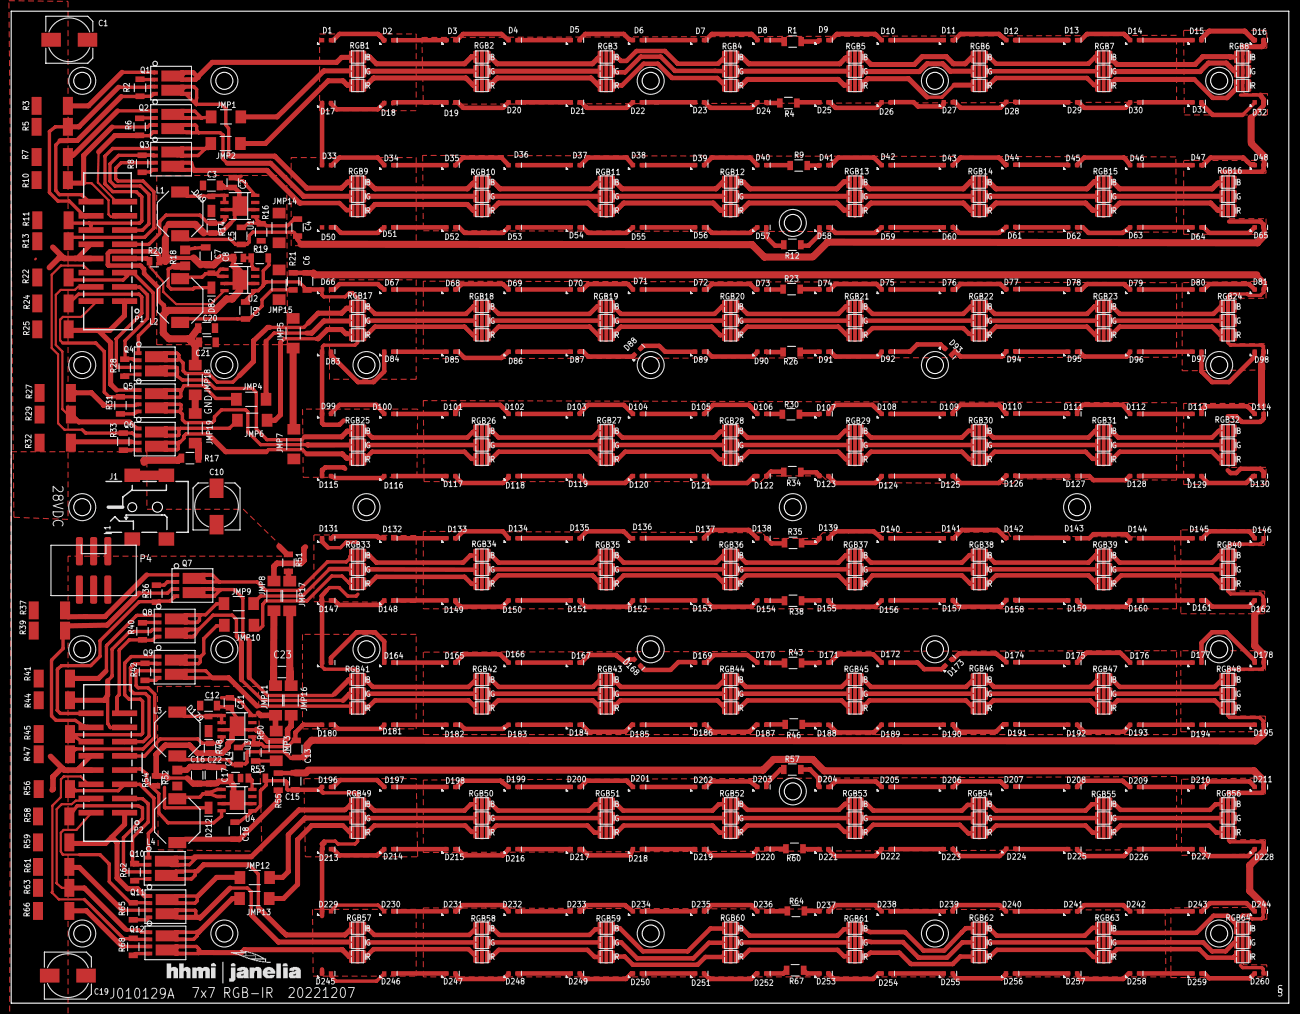
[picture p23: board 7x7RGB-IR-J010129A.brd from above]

Board: 2 copper layers, 228.3 x 177.3 mm, 485 parts (0 on the bottom side), 537 nets.

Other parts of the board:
S1, S2, S3, S4, S5, S6, S7, S8, S9, S10, S11, S12, S13, S14, S15, S16, S17, S18, S19, S20, S21, S22, S23, S24, S25, S26, S27, S28: SCREW; 4-40SOCKET

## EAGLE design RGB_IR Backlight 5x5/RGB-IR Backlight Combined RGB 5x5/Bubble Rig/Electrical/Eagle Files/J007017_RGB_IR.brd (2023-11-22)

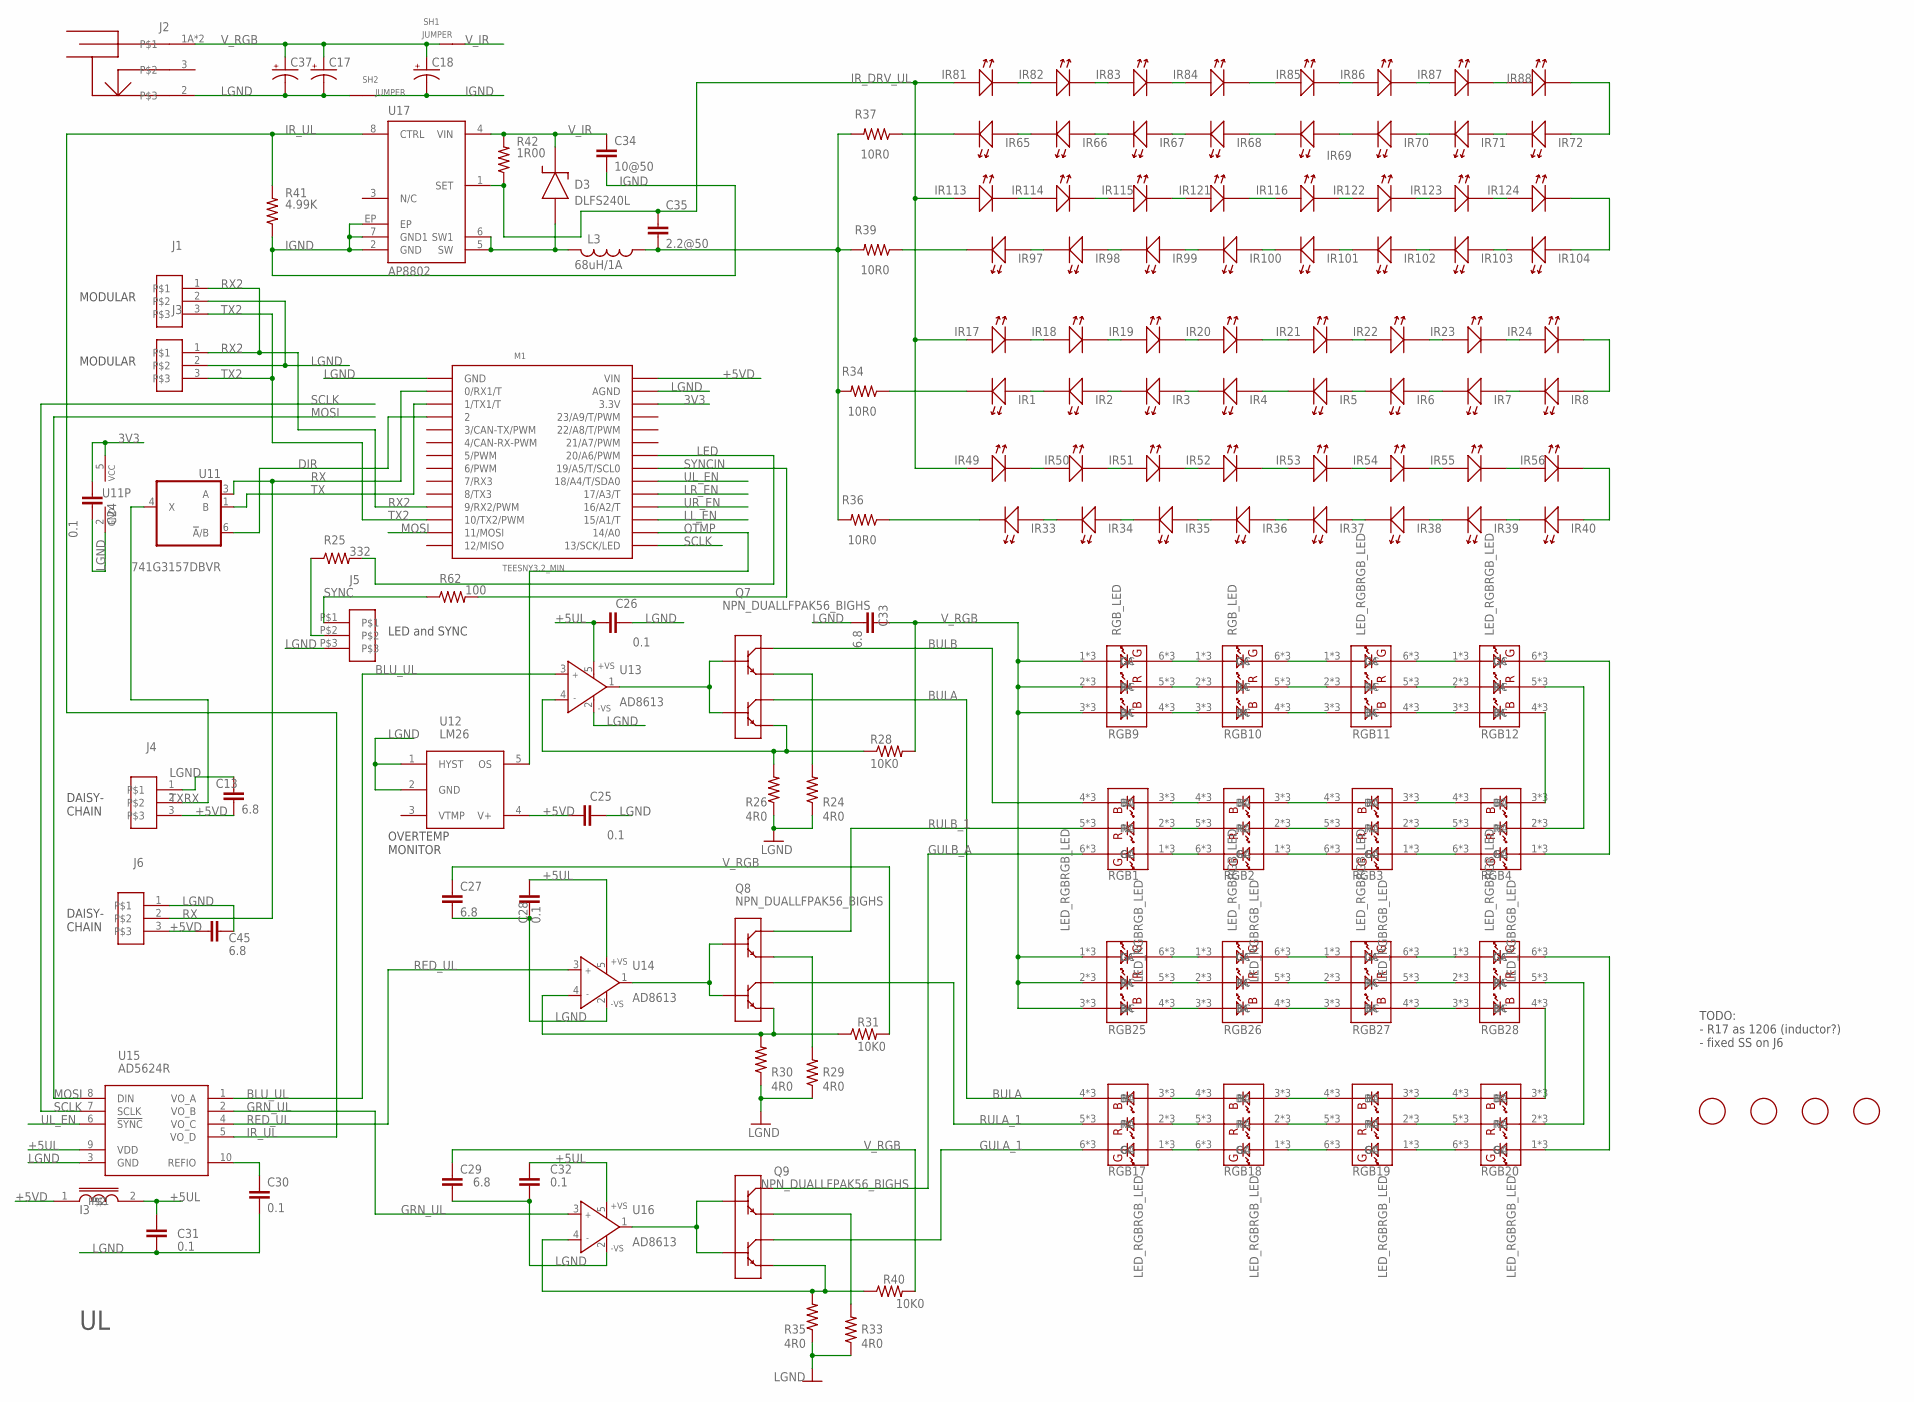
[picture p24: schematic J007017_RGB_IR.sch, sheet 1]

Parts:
$$U$1, $$U$2, $$U$3: FIDUCIAL; FIDUCIAL_1MM
C13, C27, C29, C33, C45: 6.8; 1210S
C17, C18, C37: CPOL-US153CLV-0810; 153CLV-0810
C24, C25, C26, C28, C30, C31, C32: 0.1; 0603S
C34: 10@50; 1210S
C35: 2.2@50; 1206S
D3: DLFS240L; PWRDI-123
I3: INDUCTOR0805S; 0805S
IR1: LEDLED_SFH4050_A; LED_SFH4045_HEAT_A
IR2, IR3, IR4, IR5, IR6, IR7, IR8, IR17, IR18, IR19, IR20, IR21, IR22, IR23, IR24, IR33, IR34, IR35, IR36, IR37, IR38, IR39, IR40, IR49, IR50, IR51, IR52, IR53, IR54, IR55, IR56, IR65, IR66, IR67, IR68, IR69, IR70, IR71, IR72, IR81, IR82, IR83, IR84, IR85, IR86, IR87, IR88, IR97, IR98, IR99, IR100, IR101, IR102, IR103, IR104, IR113, IR114, IR115, IR116, IR121, IR122, IR123: LEDLED_SFH4050_HEAT; LED_SFH4050_HEAT
IR124: LEDLED_SFH4050; LED_SFH4050
J1: CON3AMP-3-SM-RA-X; AMP-3-SM-RA-X
J2: POWER_JACK_SHUNTPJ-002; PJ-002
J3: CON3AMP_3_SM; AMP_3_SM
J4, J6: CON3TE-3-SM-V; TE_3_SM-V
J5: CON3DF13-3-V-SM; DF13_3_V_SM
L3: 68uH/1A; SRU8043
M1: TEESNY3.2_MIN; TEENSY3.2_MIN_SM
Q7, Q8, Q9: NPN_DUALLFPAK56_BIGHS; LFPAK56_HS2
R24, R26, R29, R30, R33, R35: 4R0; 1812
R25: 332; 0805S
R28, R31, R40: 10K0; 1206S
R34, R36, R37, R39: 10R0; 1206S
R41: 4.99K; 0805S
R42: 1R00; 1206S
R62: 100; 0805S
RGB1, RGB2, RGB3, RGB4, RGB11, RGB12, RGB17, RGB18, RGB19, RGB20, RGB25, RGB26, RGB27, RGB28: LED_RGBRGB_LED; OVSPRGB_HS_FIXED
RGB9, RGB10: RGB_LED; OVSPRGB_HS_FIXED
SH1, SH2: JUMPER
U11: 741G3157DBVR; DBV_R-PDSO-G6
U12: LM26; SOT23-5
U13, U14, U16: AD8613; SOT23-5
U15: AD5624R; MSOP10
U17: AP8802; SOIC8-EP
U$2: FIDUCIAL; FIDUCIAL_1MM

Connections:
3V3: C24.1, M1.26 (3.3V), U11.5 (VCC)
+5UL: C26.1, C28.1, C31.1, C32.1, I3.2, U13.5 (+VS), U14.5 (+VS), U15.9 (VDD), U16.5 (+VS)
+5VD: C13.2, C25.1, C45.1, I3.1, J4.3, J6.3, M1.28 (VIN), U12.4 (V+); also elsewhere on the board
BLU_UL: U13.3 (IN+), U15.1 (VO_A)
BULA: Q7.5 (C2), Q7.5A (C2), Q7.5A1 (C2), Q7.5B (C2), Q7.5C (C2), Q7.5C1 (C2), Q7.5C2 (C2), Q7.6 (C2), Q7.56 (C2), Q7.56A (C2), Q7.56B (C2), RGB17.4 (BC), RGB17.4A (BC), RGB17.4B (BC)
BULB: Q7.7 (C1), Q7.8 (C1), Q7.8A (C1), Q7.8B (C1), Q7.8C (C1), Q7.8C1 (C1), Q7.8C2 (C1), Q7.8C3 (C1), Q7.78 (C1), Q7.78A (C1), Q7.78B (C1), RGB1.4 (BC), RGB1.4A (BC), RGB1.4B (BC)
DIR: M1.4 (2), U11.6 (!A!/B)
GRN_UL: U15.2 (VO_B), U16.3 (IN+)
GULA_1: Q9.5 (C2), Q9.5A (C2), Q9.5A1 (C2), Q9.5B (C2), Q9.5C (C2), Q9.5C1 (C2), Q9.5C2 (C2), Q9.6 (C2), Q9.56 (C2), Q9.56A (C2), Q9.56B (C2), RGB17.6 (GC), RGB17.6A (GC), RGB17.6B (GC)
GULB_A: Q9.7 (C1), Q9.8 (C1), Q9.8A (C1), Q9.8B (C1), Q9.8C (C1), Q9.8C1 (C1), Q9.8C2 (C1), Q9.8C3 (C1), Q9.78 (C1), Q9.78A (C1), Q9.78B (C1), RGB1.6 (GC), RGB1.6A (GC), RGB1.6B (GC)
IGND: C18.-, C34.2, R41.1, SH2.2, U17.2 (GND), U17.7 (GND1), U17.EP; also elsewhere on the board
IR_DRV_UL: C35.1, IR17.A, IR17.A1 (A), IR49.A, IR49.A1 (A), IR81.A, IR81.A1 (A), IR113.A, IR113.A1 (A), R42.1, U17.1 (SET)
IR_RET_UL: C35.2, L3.1, R34.2, R36.2, R37.2, R39.2
IR_UL: R41.2, U15.5 (VO_D), U17.8 (CTRL)
LED: M1.22 (20/A6/PWM), R25.2
LGND: C13.1, C17.-, C24.2, C25.2, C26.2, C27.2, C28.2, C29.2, C30.2, C31.2, C32.2, C33.2, C37.-, C45.2, J1.2, J2.2, J3.2, J4.1, J5.P$3, J6.1, M1.1 (GND), M1.27 (AGND), R24.1, R26.1, R29.1, R30.1, R33.1, R35.1, SH2.1, U11.2 (GND), U12.1 (HYST), U12.2 (GND), U13.2 (-VS), U14.2 (-VS), U15.3 (GND), U16.2 (-VS); also elsewhere on the board
LL_EN: M1.17 (15/A1/T); also elsewhere on the board
LR_EN: M1.19 (17/A3/T); also elsewhere on the board
MOSI: M1.13 (11/MOSI), U15.8 (DIN); also elsewhere on the board
unnamed: IR7.A, IR7.A1 (A), IR8.C (K), IR8.C1 (K)
unnamed: IR6.A, IR6.A1 (A), IR7.C (K), IR7.C1 (K)
unnamed: IR71.A, IR71.A1 (A), IR72.C (K), IR72.C1 (K)
unnamed: IR70.A, IR70.A1 (A), IR71.C (K), IR71.C1 (K)
unnamed: IR69.A, IR69.A1 (A), IR70.C (K), IR70.C1 (K)
unnamed: IR67.A, IR67.A1 (A), IR68.C (K), IR68.C1 (K)
unnamed: IR66.A, IR66.A1 (A), IR67.C (K), IR67.C1 (K)
unnamed: IR65.A, IR65.A1 (A), IR66.C (K), IR66.C1 (K)
unnamed: IR5.A, IR5.A1 (A), IR6.C (K), IR6.C1 (K)
unnamed: IR3.A, IR3.A1 (A), IR4.C (K), IR4.C1 (K)
unnamed: IR2.A, IR2.A1 (A), IR3.C (K), IR3.C1 (K)
unnamed: IR1.A, IR1.A1 (A), IR2.C (K), IR2.C1 (K)
unnamed: IR17.C (K), IR17.C1 (K), IR18.A, IR18.A1 (A)
unnamed: IR81.C (K), IR81.C1 (K), IR82.A, IR82.A1 (A)
unnamed: IR18.C (K), IR18.C1 (K), IR19.A, IR19.A1 (A)
unnamed: IR82.C (K), IR82.C1 (K), IR83.A, IR83.A1 (A)
unnamed: IR83.C (K), IR83.C1 (K), IR84.A, IR84.A1 (A)
unnamed: IR68.A, IR68.A1 (A), IR69.C (K), IR69.C1 (K)
unnamed: IR103.A, IR103.A1 (A), IR104.C (K), IR104.C1 (K)
unnamed: IR102.A, IR102.A1 (A), IR103.C (K), IR103.C1 (K)
unnamed: IR101.A, IR101.A1 (A), IR102.C (K), IR102.C1 (K)
unnamed: IR100.A, IR100.A1 (A), IR101.C (K), IR101.C1 (K)
unnamed: IR99.A, IR99.A1 (A), IR100.C (K), IR100.C1 (K)
unnamed: IR19.C (K), IR19.C1 (K), IR20.A, IR20.A1 (A)
unnamed: IR4.A, IR4.A1 (A), IR5.C (K), IR5.C1 (K)
unnamed: IR39.A, IR39.A1 (A), IR40.C (K), IR40.C1 (K)
unnamed: IR38.A, IR38.A1 (A), IR39.C (K), IR39.C1 (K)
unnamed: IR37.A, IR37.A1 (A), IR38.C (K), IR38.C1 (K)
unnamed: IR98.A, IR98.A1 (A), IR99.C (K), IR99.C1 (K)
unnamed: IR36.A, IR36.A1 (A), IR37.C (K), IR37.C1 (K)
unnamed: IR35.A, IR35.A1 (A), IR36.C (K), IR36.C1 (K)
unnamed: IR97.A, IR97.A1 (A), IR98.C (K), IR98.C1 (K)
unnamed: IR85.C (K), IR85.C1 (K), IR86.A, IR86.A1 (A)
unnamed: IR86.C (K), IR86.C1 (K), IR87.A, IR87.A1 (A)
unnamed: IR34.A, IR34.A1 (A), IR35.C (K), IR35.C1 (K)
unnamed: IR87.C (K), IR87.C1 (K), IR88.A, IR88.A1 (A)
unnamed: IR33.A, IR33.A1 (A), IR34.C (K), IR34.C1 (K)
unnamed: IR21.C (K), IR21.C1 (K), IR22.A, IR22.A1 (A)
unnamed: IR22.C (K), IR22.C1 (K), IR23.A, IR23.A1 (A)
unnamed: IR23.C (K), IR23.C1 (K), IR24.A, IR24.A1 (A)
unnamed: IR49.C (K), IR49.C1 (K), IR50.A, IR50.A1 (A)
unnamed: IR50.C (K), IR50.C1 (K), IR51.A, IR51.A1 (A)
unnamed: IR51.C (K), IR51.C1 (K), IR52.A, IR52.A1 (A)
unnamed: IR53.C (K), IR53.C1 (K), IR54.A, IR54.A1 (A)
unnamed: IR54.C (K), IR54.C1 (K), IR55.A, IR55.A1 (A)
unnamed: IR55.C (K), IR55.C1 (K), IR56.A, IR56.A1 (A)
unnamed: IR113.C (K), IR113.C1 (K), IR114.A, IR114.A1 (A)
unnamed: IR20.C (K), IR20.C1 (K), IR21.A, IR21.A1 (A)
unnamed: IR114.C (K), IR114.C1 (K), IR115.A, IR115.A1 (A)
unnamed: IR8.A, IR8.A1 (A), IR24.C (K), IR24.C1 (K)
unnamed: IR52.C (K), IR52.C1 (K), IR53.A, IR53.A1 (A)
unnamed: IR115.C (K), IR115.C1 (K), IR121.A, IR121.A1 (A)
unnamed: IR1.C (K), R34.1
unnamed: IR40.A, IR40.A1 (A), IR56.C (K), IR56.C1 (K)
unnamed: IR33.C (K), IR33.C1 (K), R36.1
unnamed: RGB9.6 (GC), RGB9.6A (GC), RGB9.6B (GC), RGB10.1 (GA), RGB10.1A (GA), RGB10.1B (GA)
unnamed: RGB9.5 (RC), RGB9.5A (RC), RGB9.5B (RC), RGB10.2 (RA), RGB10.2A (RA), RGB10.2B (RA)
unnamed: IR65.C (K), IR65.C1 (K), R37.1
unnamed: RGB9.4 (BC), RGB9.4A (BC), RGB9.4B (BC), RGB10.3 (BA), RGB10.3A (BA), RGB10.3B (BA)
unnamed: IR116.C (K), IR116.C1 (K), IR122.A, IR122.A1 (A)
unnamed: RGB10.6 (GC), RGB10.6A (GC), RGB10.6B (GC), RGB11.1 (GA), RGB11.1A (GA), RGB11.1B (GA)
unnamed: IR122.C (K), IR122.C1 (K), IR123.A, IR123.A1 (A)
unnamed: IR123.C (K), IR123.C1 (K), IR124.A
unnamed: Q8.3 (E2), R30.2, R31.1, U14.4 (IN-)
unnamed: D3.A, L3.2, U17.5 (SW), U17.6 (SW1)
unnamed: IR84.C (K), IR84.C1 (K), IR85.A, IR85.A1 (A)
unnamed: RGB10.5 (RC), RGB10.5A (RC), RGB10.5B (RC), RGB11.2 (RA), RGB11.2A (RA), RGB11.2B (RA)
unnamed: IR72.A, IR72.A1 (A), IR88.C (K), IR88.C1 (K)
unnamed: C30.1, U15.10 (REFIO)
unnamed: IR116.A, IR116.A1 (A), IR121.C (K), IR121.C1 (K)
unnamed: RGB10.4 (BC), RGB10.4A (BC), RGB10.4B (BC), RGB11.3 (BA), RGB11.3A (BA), RGB11.3B (BA)
unnamed: RGB11.6 (GC), RGB11.6A (GC), RGB11.6B (GC), RGB12.1 (GA), RGB12.1A (GA), RGB12.1B (GA)
unnamed: IR104.A, IR104.A1 (A), IR124.C (K)
unnamed: RGB11.5 (RC), RGB11.5A (RC), RGB11.5B (RC), RGB12.2 (RA), RGB12.2A (RA), RGB12.2B (RA)
unnamed: IR97.C (K), IR97.C1 (K), R39.1
unnamed: Q9.3 (E2), R35.2, R40.1, U16.4 (IN-)
unnamed: RGB11.4 (BC), RGB11.4A (BC), RGB11.4B (BC), RGB12.3 (BA), RGB12.3A (BA), RGB12.3B (BA)
unnamed: RGB4.1 (GA), RGB4.1A (GA), RGB4.1B (GA), RGB12.6 (GC), RGB12.6A (GC), RGB12.6B (GC)
unnamed: Q8.1 (E1), R29.2
unnamed: RGB4.2 (RA), RGB4.2A (RA), RGB4.2B (RA), RGB12.5 (RC), RGB12.5A (RC), RGB12.5B (RC)
unnamed: Q8.2 (B1), Q8.4 (B2), U14.1 (OUT)
unnamed: RGB4.3 (BA), RGB4.3A (BA), RGB4.3B (BA), RGB12.4 (BC), RGB12.4A (BC), RGB12.4B (BC)
unnamed: RGB3.1 (GA), RGB3.1A (GA), RGB3.1B (GA), RGB4.6 (GC), RGB4.6A (GC), RGB4.6B (GC)
unnamed: RGB3.2 (RA), RGB3.2A (RA), RGB3.2B (RA), RGB4.5 (RC), RGB4.5A (RC), RGB4.5B (RC)
unnamed: RGB3.3 (BA), RGB3.3A (BA), RGB3.3B (BA), RGB4.4 (BC), RGB4.4A (BC), RGB4.4B (BC)
unnamed: RGB2.1 (GA), RGB2.1A (GA), RGB2.1B (GA), RGB3.6 (GC), RGB3.6A (GC), RGB3.6B (GC)
unnamed: RGB2.2 (RA), RGB2.2A (RA), RGB2.2B (RA), RGB3.5 (RC), RGB3.5A (RC), RGB3.5B (RC)
unnamed: RGB2.3 (BA), RGB2.3A (BA), RGB2.3B (BA), RGB3.4 (BC), RGB3.4A (BC), RGB3.4B (BC)
unnamed: RGB1.1 (GA), RGB1.1A (GA), RGB1.1B (GA), RGB2.6 (GC), RGB2.6A (GC), RGB2.6B (GC)
unnamed: RGB1.2 (RA), RGB1.2A (RA), RGB1.2B (RA), RGB2.5 (RC), RGB2.5A (RC), RGB2.5B (RC)
unnamed: RGB1.3 (BA), RGB1.3A (BA), RGB1.3B (BA), RGB2.4 (BC), RGB2.4A (BC), RGB2.4B (BC)
unnamed: Q9.2 (B1), Q9.4 (B2), U16.1 (OUT)
unnamed: RGB25.6 (GC), RGB25.6A (GC), RGB25.6B (GC), RGB26.1 (GA), RGB26.1A (GA), RGB26.1B (GA)
unnamed: RGB25.5 (RC), RGB25.5A (RC), RGB25.5B (RC), RGB26.2 (RA), RGB26.2A (RA), RGB26.2B (RA)
unnamed: RGB25.4 (BC), RGB25.4A (BC), RGB25.4B (BC), RGB26.3 (BA), RGB26.3A (BA), RGB26.3B (BA)
unnamed: RGB26.6 (GC), RGB26.6A (GC), RGB26.6B (GC), RGB27.1 (GA), RGB27.1A (GA), RGB27.1B (GA)
unnamed: RGB26.5 (RC), RGB26.5A (RC), RGB26.5B (RC), RGB27.2 (RA), RGB27.2A (RA), RGB27.2B (RA)
unnamed: RGB26.4 (BC), RGB26.4A (BC), RGB26.4B (BC), RGB27.3 (BA), RGB27.3A (BA), RGB27.3B (BA)
unnamed: RGB27.6 (GC), RGB27.6A (GC), RGB27.6B (GC), RGB28.1 (GA), RGB28.1A (GA), RGB28.1B (GA)
unnamed: RGB27.5 (RC), RGB27.5A (RC), RGB27.5B (RC), RGB28.2 (RA), RGB28.2A (RA), RGB28.2B (RA)
unnamed: RGB27.4 (BC), RGB27.4A (BC), RGB27.4B (BC), RGB28.3 (BA), RGB28.3A (BA), RGB28.3B (BA)
unnamed: RGB20.1 (GA), RGB20.1A (GA), RGB20.1B (GA), RGB28.6 (GC), RGB28.6A (GC), RGB28.6B (GC)
unnamed: RGB20.2 (RA), RGB20.2A (RA), RGB20.2B (RA), RGB28.5 (RC), RGB28.5A (RC), RGB28.5B (RC)
unnamed: RGB20.3 (BA), RGB20.3A (BA), RGB20.3B (BA), RGB28.4 (BC), RGB28.4A (BC), RGB28.4B (BC)
unnamed: RGB19.1 (GA), RGB19.1A (GA), RGB19.1B (GA), RGB20.6 (GC), RGB20.6A (GC), RGB20.6B (GC)
unnamed: RGB19.2 (RA), RGB19.2A (RA), RGB19.2B (RA), RGB20.5 (RC), RGB20.5A (RC), RGB20.5B (RC)
unnamed: RGB19.3 (BA), RGB19.3A (BA), RGB19.3B (BA), RGB20.4 (BC), RGB20.4A (BC), RGB20.4B (BC)
unnamed: RGB18.1 (GA), RGB18.1A (GA), RGB18.1B (GA), RGB19.6 (GC), RGB19.6A (GC), RGB19.6B (GC)
unnamed: RGB18.2 (RA), RGB18.2A (RA), RGB18.2B (RA), RGB19.5 (RC), RGB19.5A (RC), RGB19.5B (RC)
unnamed: RGB18.3 (BA), RGB18.3A (BA), RGB18.3B (BA), RGB19.4 (BC), RGB19.4A (BC), RGB19.4B (BC)
unnamed: RGB17.1 (GA), RGB17.1A (GA), RGB17.1B (GA), RGB18.6 (GC), RGB18.6A (GC), RGB18.6B (GC)
unnamed: RGB17.2 (RA), RGB17.2A (RA), RGB17.2B (RA), RGB18.5 (RC), RGB18.5A (RC), RGB18.5B (RC)
unnamed: RGB17.3 (BA), RGB17.3A (BA), RGB17.3B (BA), RGB18.4 (BC), RGB18.4A (BC), RGB18.4B (BC)
unnamed: Q7.2 (B1), Q7.4 (B2), U13.1 (OUT)
unnamed: Q7.1 (E1), R24.2
unnamed: Q9.1 (E1), R33.2
unnamed: Q7.3 (E2), R26.2, R28.1, U13.4 (IN-)
unnamed: J5.P$2, R25.1
OTMP: M1.16 (14/A0), U12.5 (OS)
RED_UL: U14.3 (IN+), U15.4 (VO_C)
RULA_1: Q8.5 (C2), Q8.5A (C2), Q8.5A1 (C2), Q8.5B (C2), Q8.5C (C2), Q8.5C1 (C2), Q8.5C2 (C2), Q8.6 (C2), Q8.56 (C2), Q8.56A (C2), Q8.56B (C2), RGB17.5 (RC), RGB17.5A (RC), RGB17.5B (RC)
RULB_1: Q8.7 (C1), Q8.8 (C1), Q8.8A (C1), Q8.8B (C1), Q8.8C (C1), Q8.8C1 (C1), Q8.8C2 (C1), Q8.8C3 (C1), Q8.78 (C1), Q8.78A (C1), Q8.78B (C1), RGB1.5 (RC), RGB1.5A (RC), RGB1.5B (RC)
RX: J6.2, M1.2 (0/RX1/T), U11.3 (A)
RX2: J1.1, J3.1, M1.11 (9/RX2/PWM)
SCLK: M1.15 (13/SCK/LED), U15.7 (SCLK); also elsewhere on the board
SYNC: J5.P$1, R62.1
SYNCIN: M1.21 (19/A5/T/SCL0), R62.2
TX: M1.3 (1/TX1/T), U11.1 (B)
TX2: J1.3, J3.3, M1.12 (10/TX2/PWM)
TXRX: J4.2, U11.4 (X)
UL_EN: M1.20 (18/A4/T/SDA0), U15.6 (!SYNC)
UR_EN: M1.18 (16/A2/T); also elsewhere on the board
V_IR: C34.1, D3.K, R42.2, SH1.1, U17.4 (VIN); also elsewhere on the board
V_RGB: C17.+, C18.+, C27.1, C29.1, C33.1, C37.+, J2.1A, J2.1B, R28.2, R31.2, R40.2, RGB9.1 (GA), RGB9.1A (GA), RGB9.1B (GA), RGB9.2 (RA), RGB9.2A (RA), RGB9.2B (RA), RGB9.3 (BA), RGB9.3A (BA), RGB9.3B (BA), RGB25.1 (GA), RGB25.1A (GA), RGB25.1B (GA), RGB25.2 (RA), RGB25.2A (RA), RGB25.2B (RA), RGB25.3 (BA), RGB25.3A (BA), RGB25.3B (BA), SH1.2; also elsewhere on the board

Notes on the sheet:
TODO: - R17 as 1206 (inductor?) - fixed SS on J6
LED and SYNC
MODULAR
DAISY- CHAIN
OVERTEMP MONITOR

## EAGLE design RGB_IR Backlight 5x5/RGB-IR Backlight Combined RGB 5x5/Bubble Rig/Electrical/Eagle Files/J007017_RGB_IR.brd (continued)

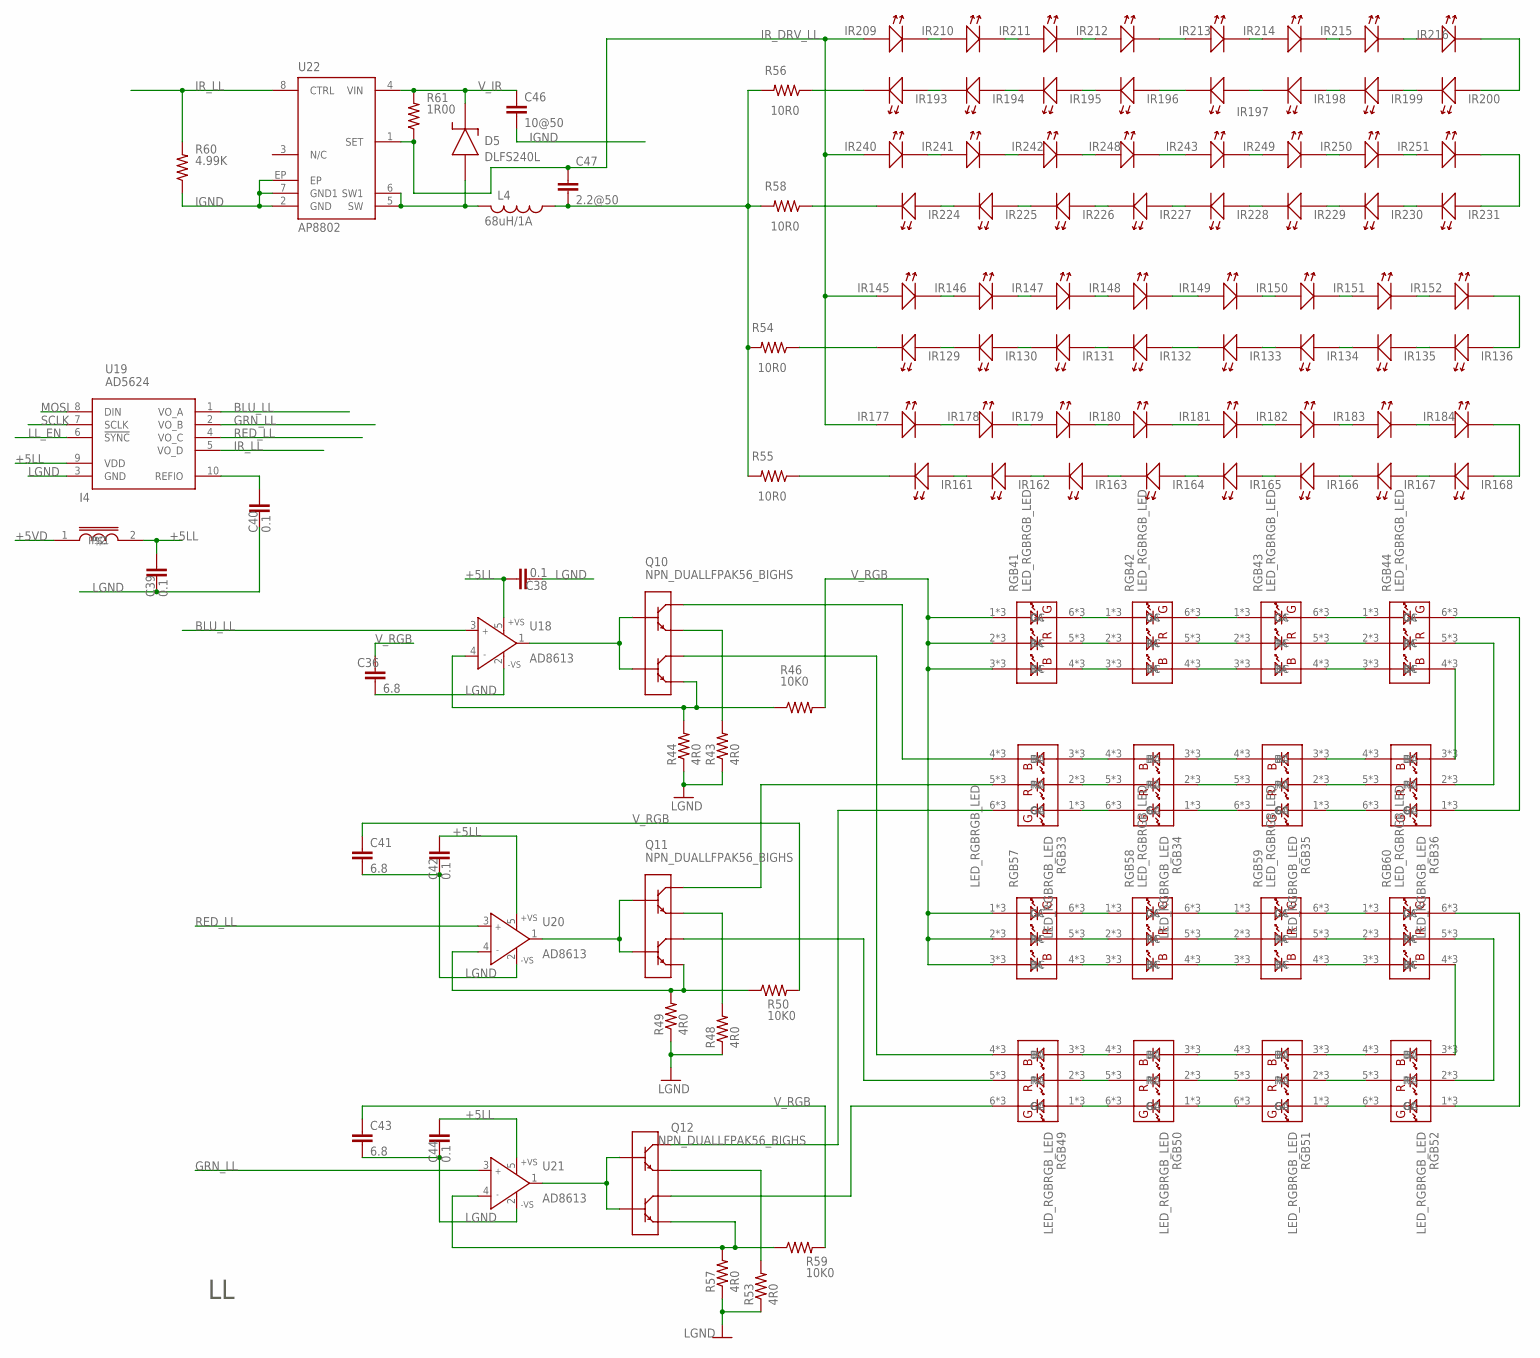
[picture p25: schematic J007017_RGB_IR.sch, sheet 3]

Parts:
C36, C41, C43: 6.8; 1210S
C38, C39, C40, C42, C44: 0.1; 0603S
C46: 10@50; 1210S
C47: 2.2@50; 1206S
D5: DLFS240L; PWRDI-123
I4: INDUCTOR0805S; 0805S
IR129: LEDLED_SFH4050_A; LED_SFH4045_HEAT_A
IR130, IR131, IR132, IR133, IR134, IR135, IR145, IR146, IR147, IR148, IR149, IR150, IR151, IR152, IR161, IR162, IR163, IR164, IR165, IR166, IR167, IR168, IR177, IR178, IR179, IR180, IR181, IR182, IR183, IR184, IR193, IR194, IR195, IR196, IR197, IR198, IR199, IR200, IR209, IR210, IR211, IR212, IR213, IR214, IR215, IR216, IR224, IR225, IR226, IR227, IR228, IR229, IR230, IR231, IR240, IR241, IR242, IR243, IR248, IR249, IR250: LEDLED_SFH4050_HEAT; LED_SFH4050_HEAT
IR136, IR251: LEDLED_SFH4050; LED_SFH4050
L4: 68uH/1A; SRU8043
Q10, Q11, Q12: NPN_DUALLFPAK56_BIGHS; LFPAK56_HS2
R43, R44, R48, R49, R53, R57: 4R0; 1812
R46, R50, R59: 10K0; 1206S
R54, R55, R56, R58: 10R0; 1206S
R60: 4.99K; 0805S
R61: 1R00; 1206S
RGB33, RGB34, RGB35, RGB36, RGB41, RGB42, RGB43, RGB44, RGB49, RGB50, RGB51, RGB52, RGB57, RGB58, RGB59, RGB60: LED_RGBRGB_LED; OVSPRGB_HS_FIXED
U18, U20, U21: AD8613; SOT23-5
U19: AD5624; MSOP10
U22: AP8802; SOIC8-EP

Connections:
+5LL: C38.1, C39.1, C42.1, C44.1, I4.2, U18.5 (+VS), U19.9 (VDD), U20.5 (+VS), U21.5 (+VS)
+5VD: I4.1; also elsewhere on the board
BLU_LL: U18.3 (IN+), U19.1 (VO_A)
GRN_LL: U19.2 (VO_B), U21.3 (IN+)
IGND: C46.2, R60.1, U22.2 (GND), U22.7 (GND1), U22.EP; also elsewhere on the board
IR_DRV_LL: C47.1, IR145.A, IR145.A1 (A), IR177.A, IR177.A1 (A), IR209.A, IR209.A1 (A), IR240.A, IR240.A1 (A), R61.1, U22.1 (SET)
IR_LL: R60.2, U19.5 (VO_D), U22.8 (CTRL)
IR_RET_UL1: C47.2, L4.1, R54.2, R55.2, R56.2, R58.2
LGND: C36.2, C38.2, C39.2, C40.2, C41.2, C42.2, C43.2, C44.2, R43.1, R44.1, R48.1, R49.1, R53.1, R57.1, U18.2 (-VS), U19.3 (GND), U20.2 (-VS), U21.2 (-VS); also elsewhere on the board
LL_EN: U19.6 (!SYNC); also elsewhere on the board
MOSI: U19.8 (DIN); also elsewhere on the board
unnamed: IR135.A, IR135.A1 (A), IR136.C (K)
unnamed: IR134.A, IR134.A1 (A), IR135.C (K), IR135.C1 (K)
unnamed: IR133.A, IR133.A1 (A), IR134.C (K), IR134.C1 (K)
unnamed: C40.1, U19.10 (REFIO)
unnamed: IR131.A, IR131.A1 (A), IR132.C (K), IR132.C1 (K)
unnamed: IR130.A, IR130.A1 (A), IR131.C (K), IR131.C1 (K)
unnamed: IR129.A, IR129.A1 (A), IR130.C (K), IR130.C1 (K)
unnamed: IR145.C (K), IR145.C1 (K), IR146.A, IR146.A1 (A)
unnamed: IR146.C (K), IR146.C1 (K), IR147.A, IR147.A1 (A)
unnamed: IR147.C (K), IR147.C1 (K), IR148.A, IR148.A1 (A)
unnamed: IR132.A, IR132.A1 (A), IR133.C (K), IR133.C1 (K)
unnamed: IR167.A, IR167.A1 (A), IR168.C (K), IR168.C1 (K)
unnamed: IR166.A, IR166.A1 (A), IR167.C (K), IR167.C1 (K)
unnamed: IR165.A, IR165.A1 (A), IR166.C (K), IR166.C1 (K)
unnamed: IR164.A, IR164.A1 (A), IR165.C (K), IR165.C1 (K)
unnamed: IR163.A, IR163.A1 (A), IR164.C (K), IR164.C1 (K)
unnamed: IR162.A, IR162.A1 (A), IR163.C (K), IR163.C1 (K)
unnamed: IR161.A, IR161.A1 (A), IR162.C (K), IR162.C1 (K)
unnamed: IR149.C (K), IR149.C1 (K), IR150.A, IR150.A1 (A)
unnamed: IR150.C (K), IR150.C1 (K), IR151.A, IR151.A1 (A)
unnamed: IR151.C (K), IR151.C1 (K), IR152.A, IR152.A1 (A)
unnamed: IR177.C (K), IR177.C1 (K), IR178.A, IR178.A1 (A)
unnamed: IR178.C (K), IR178.C1 (K), IR179.A, IR179.A1 (A)
unnamed: IR179.C (K), IR179.C1 (K), IR180.A, IR180.A1 (A)
unnamed: IR181.C (K), IR181.C1 (K), IR182.A, IR182.A1 (A)
unnamed: IR182.C (K), IR182.C1 (K), IR183.A, IR183.A1 (A)
unnamed: IR183.C (K), IR183.C1 (K), IR184.A, IR184.A1 (A)
unnamed: IR148.C (K), IR148.C1 (K), IR149.A, IR149.A1 (A)
unnamed: IR136.A, IR152.C (K), IR152.C1 (K)
unnamed: IR180.C (K), IR180.C1 (K), IR181.A, IR181.A1 (A)
unnamed: IR168.A, IR168.A1 (A), IR184.C (K), IR184.C1 (K)
unnamed: IR129.C (K), R54.1
unnamed: IR161.C (K), IR161.C1 (K), R55.1
unnamed: IR199.A, IR199.A1 (A), IR200.C (K), IR200.C1 (K)
unnamed: IR198.A, IR198.A1 (A), IR199.C (K), IR199.C1 (K)
unnamed: IR197.A, IR197.A1 (A), IR198.C (K), IR198.C1 (K)
unnamed: IR195.A, IR195.A1 (A), IR196.C (K), IR196.C1 (K)
unnamed: IR194.A, IR194.A1 (A), IR195.C (K), IR195.C1 (K)
unnamed: IR193.A, IR193.A1 (A), IR194.C (K), IR194.C1 (K)
unnamed: IR209.C (K), IR209.C1 (K), IR210.A, IR210.A1 (A)
unnamed: IR210.C (K), IR210.C1 (K), IR211.A, IR211.A1 (A)
unnamed: IR211.C (K), IR211.C1 (K), IR212.A, IR212.A1 (A)
unnamed: IR196.A, IR196.A1 (A), IR197.C (K), IR197.C1 (K)
unnamed: IR230.A, IR230.A1 (A), IR231.C (K), IR231.C1 (K)
unnamed: IR229.A, IR229.A1 (A), IR230.C (K), IR230.C1 (K)
unnamed: IR228.A, IR228.A1 (A), IR229.C (K), IR229.C1 (K)
unnamed: IR227.A, IR227.A1 (A), IR228.C (K), IR228.C1 (K)
unnamed: IR226.A, IR226.A1 (A), IR227.C (K), IR227.C1 (K)
unnamed: IR225.A, IR225.A1 (A), IR226.C (K), IR226.C1 (K)
unnamed: IR224.A, IR224.A1 (A), IR225.C (K), IR225.C1 (K)
unnamed: IR213.C (K), IR213.C1 (K), IR214.A, IR214.A1 (A)
unnamed: IR214.C (K), IR214.C1 (K), IR215.A, IR215.A1 (A)
unnamed: IR215.C (K), IR215.C1 (K), IR216.A, IR216.A1 (A)
unnamed: IR240.C (K), IR240.C1 (K), IR241.A, IR241.A1 (A)
unnamed: IR241.C (K), IR241.C1 (K), IR242.A, IR242.A1 (A)
unnamed: IR242.C (K), IR242.C1 (K), IR248.A, IR248.A1 (A)
unnamed: IR243.C (K), IR243.C1 (K), IR249.A, IR249.A1 (A)
unnamed: IR249.C (K), IR249.C1 (K), IR250.A, IR250.A1 (A)
unnamed: IR250.C (K), IR250.C1 (K), IR251.A
unnamed: IR212.C (K), IR212.C1 (K), IR213.A, IR213.A1 (A)
unnamed: IR200.A, IR200.A1 (A), IR216.C (K), IR216.C1 (K)
unnamed: IR243.A, IR243.A1 (A), IR248.C (K), IR248.C1 (K)
unnamed: IR231.A, IR231.A1 (A), IR251.C (K)
unnamed: IR193.C (K), IR193.C1 (K), R56.1
unnamed: IR224.C (K), IR224.C1 (K), R58.1
unnamed: Q10.3 (E2), R44.2, R46.1, U18.4 (IN-)
unnamed: D5.A, L4.2, U22.5 (SW), U22.6 (SW1)
unnamed: Q11.3 (E2), R49.2, R50.1, U20.4 (IN-)
unnamed: Q11.2 (B1), Q11.4 (B2), U20.1 (OUT)
unnamed: RGB41.6 (GC), RGB41.6A (GC), RGB41.6B (GC), RGB42.1 (GA), RGB42.1A (GA), RGB42.1B (GA)
unnamed: RGB41.5 (RC), RGB41.5A (RC), RGB41.5B (RC), RGB42.2 (RA), RGB42.2A (RA), RGB42.2B (RA)
unnamed: RGB41.4 (BC), RGB41.4A (BC), RGB41.4B (BC), RGB42.3 (BA), RGB42.3A (BA), RGB42.3B (BA)
unnamed: RGB42.6 (GC), RGB42.6A (GC), RGB42.6B (GC), RGB43.1 (GA), RGB43.1A (GA), RGB43.1B (GA)
unnamed: RGB42.5 (RC), RGB42.5A (RC), RGB42.5B (RC), RGB43.2 (RA), RGB43.2A (RA), RGB43.2B (RA)
unnamed: RGB42.4 (BC), RGB42.4A (BC), RGB42.4B (BC), RGB43.3 (BA), RGB43.3A (BA), RGB43.3B (BA)
unnamed: RGB43.6 (GC), RGB43.6A (GC), RGB43.6B (GC), RGB44.1 (GA), RGB44.1A (GA), RGB44.1B (GA)
unnamed: RGB43.5 (RC), RGB43.5A (RC), RGB43.5B (RC), RGB44.2 (RA), RGB44.2A (RA), RGB44.2B (RA)
unnamed: RGB43.4 (BC), RGB43.4A (BC), RGB43.4B (BC), RGB44.3 (BA), RGB44.3A (BA), RGB44.3B (BA)
unnamed: RGB36.1 (GA), RGB36.1A (GA), RGB36.1B (GA), RGB44.6 (GC), RGB44.6A (GC), RGB44.6B (GC)
unnamed: RGB36.2 (RA), RGB36.2A (RA), RGB36.2B (RA), RGB44.5 (RC), RGB44.5A (RC), RGB44.5B (RC)
unnamed: RGB36.3 (BA), RGB36.3A (BA), RGB36.3B (BA), RGB44.4 (BC), RGB44.4A (BC), RGB44.4B (BC)
unnamed: RGB35.1 (GA), RGB35.1A (GA), RGB35.1B (GA), RGB36.6 (GC), RGB36.6A (GC), RGB36.6B (GC)
unnamed: RGB35.2 (RA), RGB35.2A (RA), RGB35.2B (RA), RGB36.5 (RC), RGB36.5A (RC), RGB36.5B (RC)
unnamed: RGB35.3 (BA), RGB35.3A (BA), RGB35.3B (BA), RGB36.4 (BC), RGB36.4A (BC), RGB36.4B (BC)
unnamed: RGB34.1 (GA), RGB34.1A (GA), RGB34.1B (GA), RGB35.6 (GC), RGB35.6A (GC), RGB35.6B (GC)
unnamed: RGB34.2 (RA), RGB34.2A (RA), RGB34.2B (RA), RGB35.5 (RC), RGB35.5A (RC), RGB35.5B (RC)
unnamed: RGB34.3 (BA), RGB34.3A (BA), RGB34.3B (BA), RGB35.4 (BC), RGB35.4A (BC), RGB35.4B (BC)
unnamed: RGB33.1 (GA), RGB33.1A (GA), RGB33.1B (GA), RGB34.6 (GC), RGB34.6A (GC), RGB34.6B (GC)
unnamed: RGB33.2 (RA), RGB33.2A (RA), RGB33.2B (RA), RGB34.5 (RC), RGB34.5A (RC), RGB34.5B (RC)
unnamed: RGB33.3 (BA), RGB33.3A (BA), RGB33.3B (BA), RGB34.4 (BC), RGB34.4A (BC), RGB34.4B (BC)
unnamed: Q12.3 (E2), R57.2, R59.1, U21.4 (IN-)
unnamed: Q12.2 (B1), Q12.4 (B2), U21.1 (OUT)
unnamed: RGB57.6 (GC), RGB57.6A (GC), RGB57.6B (GC), RGB58.1 (GA), RGB58.1A (GA), RGB58.1B (GA)
unnamed: RGB57.5 (RC), RGB57.5A (RC), RGB57.5B (RC), RGB58.2 (RA), RGB58.2A (RA), RGB58.2B (RA)
unnamed: RGB57.4 (BC), RGB57.4A (BC), RGB57.4B (BC), RGB58.3 (BA), RGB58.3A (BA), RGB58.3B (BA)
unnamed: RGB58.6 (GC), RGB58.6A (GC), RGB58.6B (GC), RGB59.1 (GA), RGB59.1A (GA), RGB59.1B (GA)
unnamed: RGB58.5 (RC), RGB58.5A (RC), RGB58.5B (RC), RGB59.2 (RA), RGB59.2A (RA), RGB59.2B (RA)
unnamed: RGB58.4 (BC), RGB58.4A (BC), RGB58.4B (BC), RGB59.3 (BA), RGB59.3A (BA), RGB59.3B (BA)
unnamed: RGB59.6 (GC), RGB59.6A (GC), RGB59.6B (GC), RGB60.1 (GA), RGB60.1A (GA), RGB60.1B (GA)
unnamed: RGB59.5 (RC), RGB59.5A (RC), RGB59.5B (RC), RGB60.2 (RA), RGB60.2A (RA), RGB60.2B (RA)
unnamed: RGB59.4 (BC), RGB59.4A (BC), RGB59.4B (BC), RGB60.3 (BA), RGB60.3A (BA), RGB60.3B (BA)
unnamed: RGB52.1 (GA), RGB52.1A (GA), RGB52.1B (GA), RGB60.6 (GC), RGB60.6A (GC), RGB60.6B (GC)
unnamed: RGB52.2 (RA), RGB52.2A (RA), RGB52.2B (RA), RGB60.5 (RC), RGB60.5A (RC), RGB60.5B (RC)
unnamed: RGB52.3 (BA), RGB52.3A (BA), RGB52.3B (BA), RGB60.4 (BC), RGB60.4A (BC), RGB60.4B (BC)
unnamed: RGB51.1 (GA), RGB51.1A (GA), RGB51.1B (GA), RGB52.6 (GC), RGB52.6A (GC), RGB52.6B (GC)
unnamed: RGB51.2 (RA), RGB51.2A (RA), RGB51.2B (RA), RGB52.5 (RC), RGB52.5A (RC), RGB52.5B (RC)
unnamed: RGB51.3 (BA), RGB51.3A (BA), RGB51.3B (BA), RGB52.4 (BC), RGB52.4A (BC), RGB52.4B (BC)
unnamed: RGB50.1 (GA), RGB50.1A (GA), RGB50.1B (GA), RGB51.6 (GC), RGB51.6A (GC), RGB51.6B (GC)
unnamed: RGB50.2 (RA), RGB50.2A (RA), RGB50.2B (RA), RGB51.5 (RC), RGB51.5A (RC), RGB51.5B (RC)
unnamed: RGB50.3 (BA), RGB50.3A (BA), RGB50.3B (BA), RGB51.4 (BC), RGB51.4A (BC), RGB51.4B (BC)
unnamed: RGB49.1 (GA), RGB49.1A (GA), RGB49.1B (GA), RGB50.6 (GC), RGB50.6A (GC), RGB50.6B (GC)
unnamed: RGB49.2 (RA), RGB49.2A (RA), RGB49.2B (RA), RGB50.5 (RC), RGB50.5A (RC), RGB50.5B (RC)
unnamed: RGB49.3 (BA), RGB49.3A (BA), RGB49.3B (BA), RGB50.4 (BC), RGB50.4A (BC), RGB50.4B (BC)
unnamed: Q10.2 (B1), Q10.4 (B2), U18.1 (OUT)
unnamed: Q10.1 (E1), R43.2
unnamed: Q11.1 (E1), R48.2
unnamed: Q12.1 (E1), R53.2
Q4A: Q10.7 (C1), Q10.8 (C1), Q10.8A (C1), Q10.8B (C1), Q10.8C (C1), Q10.8C1 (C1), Q10.8C2 (C1), Q10.8C3 (C1), Q10.78 (C1), Q10.78A (C1), Q10.78B (C1), RGB33.4 (BC), RGB33.4A (BC), RGB33.4B (BC)
Q4B: Q10.5 (C2), Q10.5A (C2), Q10.5A1 (C2), Q10.5B (C2), Q10.5C (C2), Q10.5C1 (C2), Q10.5C2 (C2), Q10.6 (C2), Q10.56 (C2), Q10.56A (C2), Q10.56B (C2), RGB49.4 (BC), RGB49.4A (BC), RGB49.4B (BC)
Q5A: Q11.7 (C1), Q11.8 (C1), Q11.8A (C1), Q11.8B (C1), Q11.8C (C1), Q11.8C1 (C1), Q11.8C2 (C1), Q11.8C3 (C1), Q11.78 (C1), Q11.78A (C1), Q11.78B (C1), RGB33.5 (RC), RGB33.5A (RC), RGB33.5B (RC)
Q5B: Q11.5 (C2), Q11.5A (C2), Q11.5A1 (C2), Q11.5B (C2), Q11.5C (C2), Q11.5C1 (C2), Q11.5C2 (C2), Q11.6 (C2), Q11.56 (C2), Q11.56A (C2), Q11.56B (C2), RGB49.5 (RC), RGB49.5A (RC), RGB49.5B (RC)
Q6A: Q12.7 (C1), Q12.8 (C1), Q12.8A (C1), Q12.8B (C1), Q12.8C (C1), Q12.8C1 (C1), Q12.8C2 (C1), Q12.8C3 (C1), Q12.78 (C1), Q12.78A (C1), Q12.78B (C1), RGB33.6 (GC), RGB33.6A (GC), RGB33.6B (GC)
Q6B: Q12.5 (C2), Q12.5A (C2), Q12.5A1 (C2), Q12.5B (C2), Q12.5C (C2), Q12.5C1 (C2), Q12.5C2 (C2), Q12.6 (C2), Q12.56 (C2), Q12.56A (C2), Q12.56B (C2), RGB49.6 (GC), RGB49.6A (GC), RGB49.6B (GC)
RED_LL: U19.4 (VO_C), U20.3 (IN+)
SCLK: U19.7 (SCLK); also elsewhere on the board
V_IR: C46.1, D5.K, R61.2, U22.4 (VIN); also elsewhere on the board
V_RGB: C36.1, C41.1, C43.1, R46.2, R50.2, R59.2, RGB41.1 (GA), RGB41.1A (GA), RGB41.1B (GA), RGB41.2 (RA), RGB41.2A (RA), RGB41.2B (RA), RGB41.3 (BA), RGB41.3A (BA), RGB41.3B (BA), RGB57.1 (GA), RGB57.1A (GA), RGB57.1B (GA), RGB57.2 (RA), RGB57.2A (RA), RGB57.2B (RA), RGB57.3 (BA), RGB57.3A (BA), RGB57.3B (BA); also elsewhere on the board

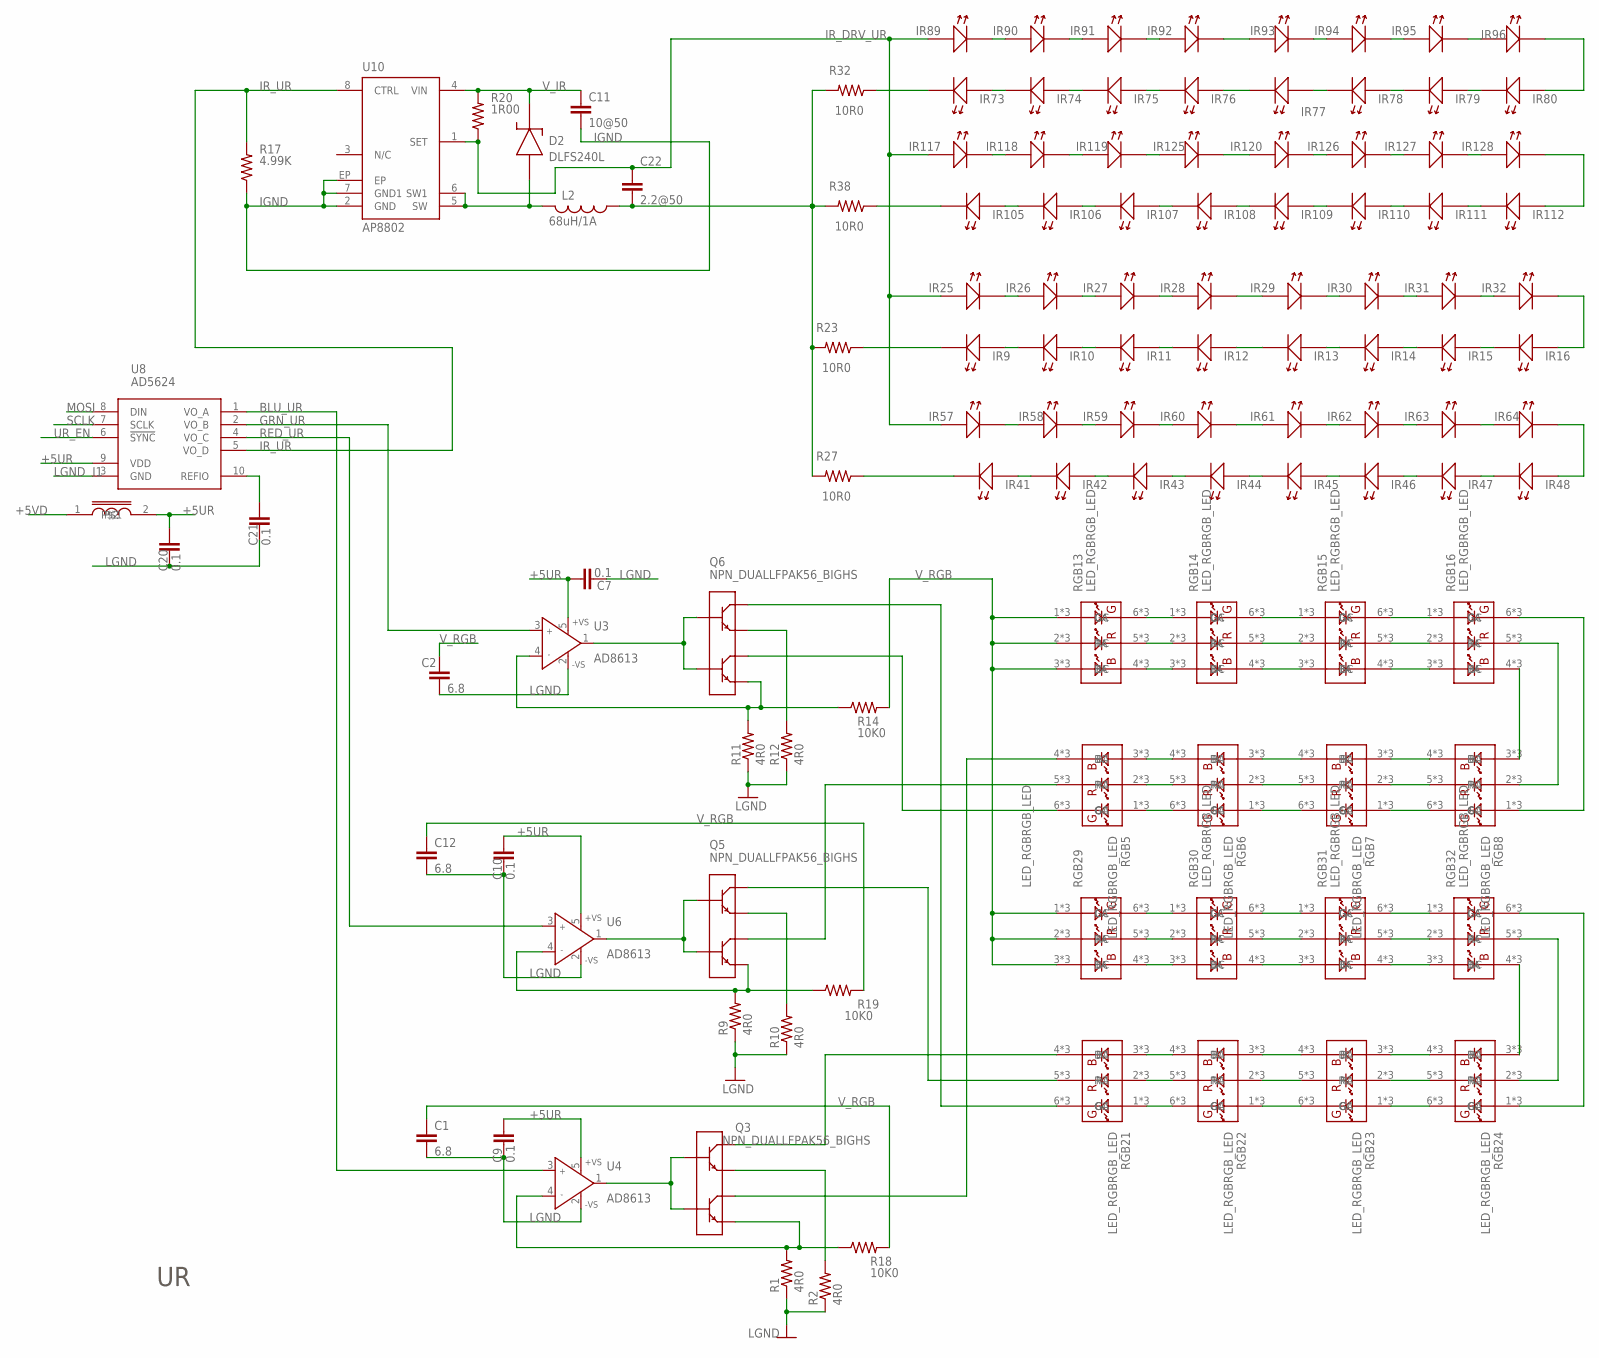
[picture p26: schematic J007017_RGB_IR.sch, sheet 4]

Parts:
C1, C2, C12: 6.8; 1210S
C7, C9, C10, C20, C21: 0.1; 0603S
C11: 10@50; 1210S
C22: 2.2@50; 1206S
D2: DLFS240L; PWRDI-123
I1: INDUCTOR0805S; 0805S
IR9, IR10, IR11, IR12, IR13, IR14, IR15, IR16, IR25, IR26, IR27, IR28, IR29, IR30, IR31, IR32, IR41, IR42, IR43, IR44, IR45, IR46, IR47, IR48, IR57, IR58, IR59, IR60, IR61, IR62, IR63, IR64, IR73, IR74, IR75, IR76, IR77, IR78, IR79, IR80, IR89, IR90, IR91, IR92, IR93, IR94, IR95, IR96, IR105, IR107, IR108, IR109, IR110, IR111, IR112, IR118, IR119, IR120, IR125, IR126, IR127: LEDLED_SFH4050_HEAT; LED_SFH4050_HEAT
IR106: LEDLED_SFH4050_C; LED_SFH4050_HEAT_C
IR117, IR128: LEDLED_SFH4050; LED_SFH4050
L2: 68uH/1A; SRU8043
Q3, Q5, Q6: NPN_DUALLFPAK56_BIGHS; LFPAK56_HS2
R1, R2, R9, R10, R11, R12: 4R0; 1812
R14, R18, R19: 10K0; 1206S
R17: 4.99K; 0805S
R20: 1R00; 1206S
R23, R27, R32, R38: 10R0; 1206S
RGB5, RGB6, RGB7, RGB8, RGB13, RGB14, RGB15, RGB16, RGB21, RGB22, RGB23, RGB24, RGB29, RGB30, RGB31, RGB32: LED_RGBRGB_LED; OVSPRGB_HS_FIXED
U3, U4, U6: AD8613; SOT23-5
U8: AD5624; MSOP10
U10: AP8802; SOIC8-EP
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

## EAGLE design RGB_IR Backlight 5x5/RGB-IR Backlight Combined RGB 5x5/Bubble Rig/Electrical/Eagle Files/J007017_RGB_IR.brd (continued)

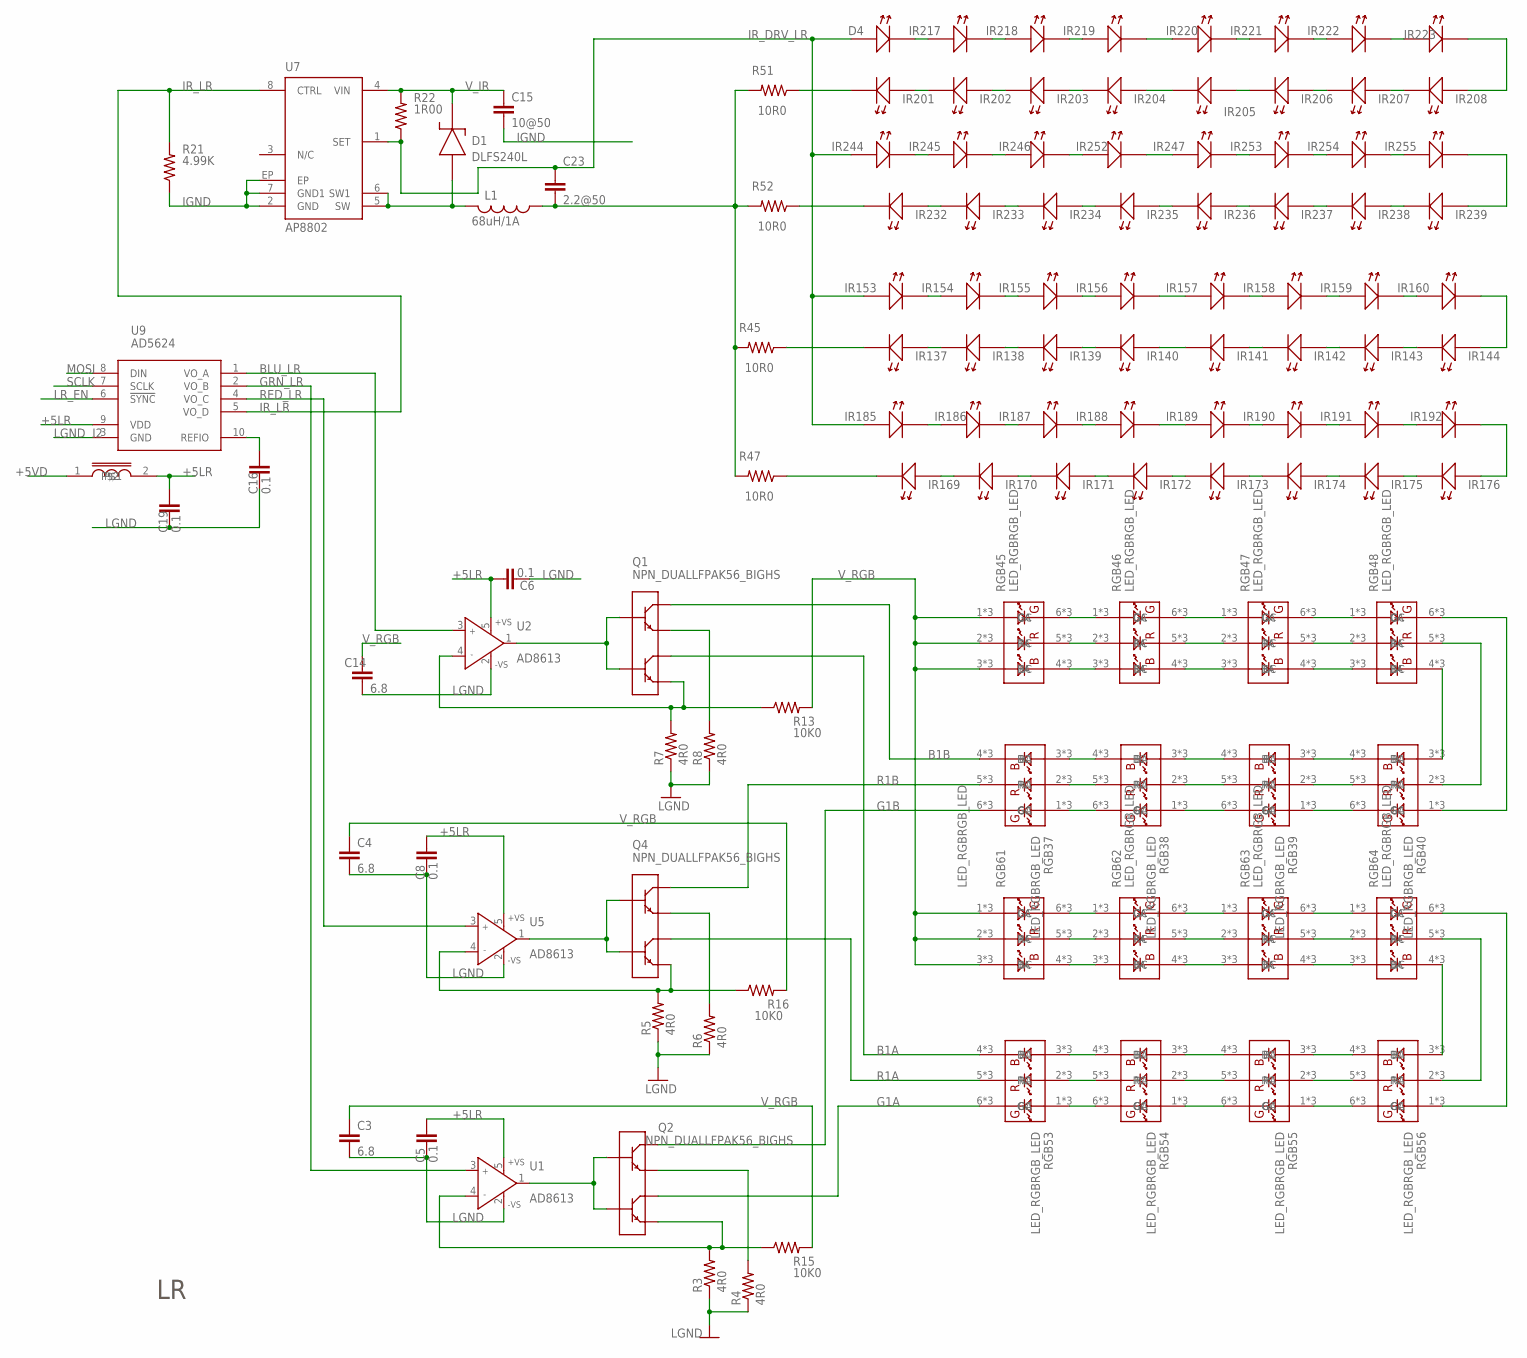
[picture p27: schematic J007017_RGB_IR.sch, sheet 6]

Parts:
C3, C4, C14: 6.8; 1210S
C5, C6, C8, C16, C19: 0.1; 0603S
C15: 10@50; 1210S
C23: 2.2@50; 1206S
D1: DLFS240L; PWRDI-123
D4: LEDLED_SFH4050_HEAT; LED_SFH4050_HEAT
I2: INDUCTOR0805S; 0805S
IR137, IR255: LEDLED_SFH4050; LED_SFH4050
IR138, IR139, IR140, IR141, IR142, IR143, IR144, IR153, IR155, IR156, IR157, IR158, IR159, IR160, IR169, IR170, IR171, IR172, IR173, IR174, IR175, IR176, IR185, IR186, IR187, IR188, IR189, IR190, IR191, IR192, IR201, IR202, IR203, IR204, IR205, IR206, IR207, IR208, IR217, IR218, IR219, IR220, IR221, IR222, IR223, IR232, IR233, IR234, IR235, IR236, IR237, IR238, IR239, IR244, IR245, IR246, IR247, IR252, IR253, IR254: LEDLED_SFH4050_HEAT; LED_SFH4050_HEAT
IR154: LEDLED_SFH4050_A; LED_SFH4045_HEAT_A
L1: 68uH/1A; SRU8043
Q1, Q2, Q4: NPN_DUALLFPAK56_BIGHS; LFPAK56_HS2
R3, R4, R5, R6, R7, R8: 4R0; 1812
R13, R15, R16: 10K0; 1206S
R21: 4.99K; 0805S
R22: 1R00; 1206S
R45, R47, R51, R52: 10R0; 1206S
RGB37, RGB38, RGB39, RGB40, RGB45, RGB46, RGB47, RGB48, RGB53, RGB54, RGB55, RGB56, RGB61, RGB62, RGB63, RGB64: LED_RGBRGB_LED; OVSPRGB_HS_FIXED
U1, U2, U5: AD8613; SOT23-5
U7: AP8802; SOIC8-EP
U9: AD5624; MSOP10

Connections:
+5LR: C5.1, C6.1, C8.1, C19.1, I2.2, U1.5 (+VS), U2.5 (+VS), U5.5 (+VS), U9.9 (VDD)
+5VD: I2.1; also elsewhere on the board
B1A: Q1.5 (C2), Q1.5A (C2), Q1.5A1 (C2), Q1.5B (C2), Q1.5C (C2), Q1.5C1 (C2), Q1.5C2 (C2), Q1.6 (C2), Q1.56 (C2), Q1.56A (C2), Q1.56B (C2), RGB53.4 (BC), RGB53.4A (BC), RGB53.4B (BC)
B1B: Q1.7 (C1), Q1.8 (C1), Q1.8A (C1), Q1.8B (C1), Q1.8C (C1), Q1.8C1 (C1), Q1.8C2 (C1), Q1.8C3 (C1), Q1.78 (C1), Q1.78A (C1), Q1.78B (C1), RGB37.4 (BC), RGB37.4A (BC), RGB37.4B (BC)
BLU_LR: U2.3 (IN+), U9.1 (VO_A)
G1A: Q2.5 (C2), Q2.5A (C2), Q2.5A1 (C2), Q2.5B (C2), Q2.5C (C2), Q2.5C1 (C2), Q2.5C2 (C2), Q2.6 (C2), Q2.56 (C2), Q2.56A (C2), Q2.56B (C2), RGB53.6 (GC), RGB53.6A (GC), RGB53.6B (GC)
G1B: Q2.7 (C1), Q2.8 (C1), Q2.8A (C1), Q2.8B (C1), Q2.8C (C1), Q2.8C1 (C1), Q2.8C2 (C1), Q2.8C3 (C1), Q2.78 (C1), Q2.78A (C1), Q2.78B (C1), RGB37.6 (GC), RGB37.6A (GC), RGB37.6B (GC)
GRN_LR: U1.3 (IN+), U9.2 (VO_B)
IGND: C15.2, R21.1, U7.2 (GND), U7.7 (GND1), U7.EP; also elsewhere on the board
IR_DRV_LR: C23.1, D4.A, D4.A1 (A), IR153.A, IR153.A1 (A), IR185.A, IR185.A1 (A), IR244.A, IR244.A1 (A), R22.1, U7.1 (SET)
IR_LR: R21.2, U7.8 (CTRL), U9.5 (VO_D)
IR_RET_UL3: C23.2, L1.1, R45.2, R47.2, R51.2, R52.2
LGND: C3.2, C4.2, C5.2, C6.2, C8.2, C14.2, C16.2, C19.2, R3.1, R4.1, R5.1, R6.1, R7.1, R8.1, U1.2 (-VS), U2.2 (-VS), U5.2 (-VS), U9.3 (GND); also elsewhere on the board
LR_EN: U9.6 (!SYNC); also elsewhere on the board
MOSI: U9.8 (DIN); also elsewhere on the board
unnamed: C16.1, U9.10 (REFIO)
unnamed: IR143.A, IR143.A1 (A), IR144.C (K), IR144.C1 (K)
unnamed: IR142.A, IR142.A1 (A), IR143.C (K), IR143.C1 (K)
unnamed: IR141.A, IR141.A1 (A), IR142.C (K), IR142.C1 (K)
unnamed: IR139.A, IR139.A1 (A), IR140.C (K), IR140.C1 (K)
unnamed: IR138.A, IR138.A1 (A), IR139.C (K), IR139.C1 (K)
unnamed: IR137.A, IR138.C (K), IR138.C1 (K)
unnamed: IR153.C (K), IR153.C1 (K), IR154.A, IR154.A1 (A)
unnamed: IR154.C (K), IR155.A, IR155.A1 (A)
unnamed: IR155.C (K), IR155.C1 (K), IR156.A, IR156.A1 (A)
unnamed: IR140.A, IR140.A1 (A), IR141.C (K), IR141.C1 (K)
unnamed: IR175.A, IR175.A1 (A), IR176.C (K), IR176.C1 (K)
unnamed: IR174.A, IR174.A1 (A), IR175.C (K), IR175.C1 (K)
unnamed: IR173.A, IR173.A1 (A), IR174.C (K), IR174.C1 (K)
unnamed: IR172.A, IR172.A1 (A), IR173.C (K), IR173.C1 (K)
unnamed: IR171.A, IR171.A1 (A), IR172.C (K), IR172.C1 (K)
unnamed: IR170.A, IR170.A1 (A), IR171.C (K), IR171.C1 (K)
unnamed: IR169.A, IR169.A1 (A), IR170.C (K), IR170.C1 (K)
unnamed: IR157.C (K), IR157.C1 (K), IR158.A, IR158.A1 (A)
unnamed: IR158.C (K), IR158.C1 (K), IR159.A, IR159.A1 (A)
unnamed: IR159.C (K), IR159.C1 (K), IR160.A, IR160.A1 (A)
unnamed: IR185.C (K), IR185.C1 (K), IR186.A, IR186.A1 (A)
unnamed: IR186.C (K), IR186.C1 (K), IR187.A, IR187.A1 (A)
unnamed: IR187.C (K), IR187.C1 (K), IR188.A, IR188.A1 (A)
unnamed: IR189.C (K), IR189.C1 (K), IR190.A, IR190.A1 (A)
unnamed: IR190.C (K), IR190.C1 (K), IR191.A, IR191.A1 (A)
unnamed: IR191.C (K), IR191.C1 (K), IR192.A, IR192.A1 (A)
unnamed: IR156.C (K), IR156.C1 (K), IR157.A, IR157.A1 (A)
unnamed: IR144.A, IR144.A1 (A), IR160.C (K), IR160.C1 (K)
unnamed: IR188.C (K), IR188.C1 (K), IR189.A, IR189.A1 (A)
unnamed: IR176.A, IR176.A1 (A), IR192.C (K), IR192.C1 (K)
unnamed: IR137.C (K), R45.1
unnamed: IR169.C (K), IR169.C1 (K), R47.1
unnamed: IR207.A, IR207.A1 (A), IR208.C (K), IR208.C1 (K)
unnamed: IR206.A, IR206.A1 (A), IR207.C (K), IR207.C1 (K)
unnamed: IR205.A, IR205.A1 (A), IR206.C (K), IR206.C1 (K)
unnamed: IR203.A, IR203.A1 (A), IR204.C (K), IR204.C1 (K)
unnamed: IR202.A, IR202.A1 (A), IR203.C (K), IR203.C1 (K)
unnamed: IR201.A, IR201.A1 (A), IR202.C (K), IR202.C1 (K)
unnamed: D4.C (K), D4.C1 (K), IR217.A, IR217.A1 (A)
unnamed: IR217.C (K), IR217.C1 (K), IR218.A, IR218.A1 (A)
unnamed: IR218.C (K), IR218.C1 (K), IR219.A, IR219.A1 (A)
unnamed: IR204.A, IR204.A1 (A), IR205.C (K), IR205.C1 (K)
unnamed: IR238.A, IR238.A1 (A), IR239.C (K), IR239.C1 (K)
unnamed: IR237.A, IR237.A1 (A), IR238.C (K), IR238.C1 (K)
unnamed: IR236.A, IR236.A1 (A), IR237.C (K), IR237.C1 (K)
unnamed: IR235.A, IR235.A1 (A), IR236.C (K), IR236.C1 (K)
unnamed: IR234.A, IR234.A1 (A), IR235.C (K), IR235.C1 (K)
unnamed: IR233.A, IR233.A1 (A), IR234.C (K), IR234.C1 (K)
unnamed: IR232.A, IR232.A1 (A), IR233.C (K), IR233.C1 (K)
unnamed: IR220.C (K), IR220.C1 (K), IR221.A, IR221.A1 (A)
unnamed: IR221.C (K), IR221.C1 (K), IR222.A, IR222.A1 (A)
unnamed: IR222.C (K), IR222.C1 (K), IR223.A, IR223.A1 (A)
unnamed: IR244.C (K), IR244.C1 (K), IR245.A, IR245.A1 (A)
unnamed: IR245.C (K), IR245.C1 (K), IR246.A, IR246.A1 (A)
unnamed: IR246.C (K), IR246.C1 (K), IR252.A, IR252.A1 (A)
unnamed: IR247.C (K), IR247.C1 (K), IR253.A, IR253.A1 (A)
unnamed: IR253.C (K), IR253.C1 (K), IR254.A, IR254.A1 (A)
unnamed: IR254.C (K), IR254.C1 (K), IR255.A
unnamed: IR219.C (K), IR219.C1 (K), IR220.A, IR220.A1 (A)
unnamed: IR208.A, IR208.A1 (A), IR223.C (K), IR223.C1 (K)
unnamed: IR247.A, IR247.A1 (A), IR252.C (K), IR252.C1 (K)
unnamed: IR239.A, IR239.A1 (A), IR255.C (K)
unnamed: IR201.C (K), IR201.C1 (K), R51.1
unnamed: IR232.C (K), IR232.C1 (K), R52.1
unnamed: Q1.3 (E2), R7.2, R13.1, U2.4 (IN-)
unnamed: D1.A, L1.2, U7.5 (SW), U7.6 (SW1)
unnamed: Q4.3 (E2), R5.2, R16.1, U5.4 (IN-)
unnamed: Q4.2 (B1), Q4.4 (B2), U5.1 (OUT)
unnamed: RGB45.6 (GC), RGB45.6A (GC), RGB45.6B (GC), RGB46.1 (GA), RGB46.1A (GA), RGB46.1B (GA)
unnamed: RGB45.5 (RC), RGB45.5A (RC), RGB45.5B (RC), RGB46.2 (RA), RGB46.2A (RA), RGB46.2B (RA)
unnamed: RGB45.4 (BC), RGB45.4A (BC), RGB45.4B (BC), RGB46.3 (BA), RGB46.3A (BA), RGB46.3B (BA)
unnamed: RGB46.6 (GC), RGB46.6A (GC), RGB46.6B (GC), RGB47.1 (GA), RGB47.1A (GA), RGB47.1B (GA)
unnamed: RGB46.5 (RC), RGB46.5A (RC), RGB46.5B (RC), RGB47.2 (RA), RGB47.2A (RA), RGB47.2B (RA)
unnamed: RGB46.4 (BC), RGB46.4A (BC), RGB46.4B (BC), RGB47.3 (BA), RGB47.3A (BA), RGB47.3B (BA)
unnamed: RGB47.6 (GC), RGB47.6A (GC), RGB47.6B (GC), RGB48.1 (GA), RGB48.1A (GA), RGB48.1B (GA)
unnamed: RGB47.5 (RC), RGB47.5A (RC), RGB47.5B (RC), RGB48.2 (RA), RGB48.2A (RA), RGB48.2B (RA)
unnamed: RGB47.4 (BC), RGB47.4A (BC), RGB47.4B (BC), RGB48.3 (BA), RGB48.3A (BA), RGB48.3B (BA)
unnamed: RGB40.1 (GA), RGB40.1A (GA), RGB40.1B (GA), RGB48.6 (GC), RGB48.6A (GC), RGB48.6B (GC)
unnamed: RGB40.2 (RA), RGB40.2A (RA), RGB40.2B (RA), RGB48.5 (RC), RGB48.5A (RC), RGB48.5B (RC)
unnamed: RGB40.3 (BA), RGB40.3A (BA), RGB40.3B (BA), RGB48.4 (BC), RGB48.4A (BC), RGB48.4B (BC)
unnamed: RGB39.1 (GA), RGB39.1A (GA), RGB39.1B (GA), RGB40.6 (GC), RGB40.6A (GC), RGB40.6B (GC)
unnamed: RGB39.2 (RA), RGB39.2A (RA), RGB39.2B (RA), RGB40.5 (RC), RGB40.5A (RC), RGB40.5B (RC)
unnamed: RGB39.3 (BA), RGB39.3A (BA), RGB39.3B (BA), RGB40.4 (BC), RGB40.4A (BC), RGB40.4B (BC)
unnamed: RGB38.1 (GA), RGB38.1A (GA), RGB38.1B (GA), RGB39.6 (GC), RGB39.6A (GC), RGB39.6B (GC)
unnamed: RGB38.2 (RA), RGB38.2A (RA), RGB38.2B (RA), RGB39.5 (RC), RGB39.5A (RC), RGB39.5B (RC)
unnamed: RGB38.3 (BA), RGB38.3A (BA), RGB38.3B (BA), RGB39.4 (BC), RGB39.4A (BC), RGB39.4B (BC)
unnamed: RGB37.1 (GA), RGB37.1A (GA), RGB37.1B (GA), RGB38.6 (GC), RGB38.6A (GC), RGB38.6B (GC)
unnamed: RGB37.2 (RA), RGB37.2A (RA), RGB37.2B (RA), RGB38.5 (RC), RGB38.5A (RC), RGB38.5B (RC)
unnamed: RGB37.3 (BA), RGB37.3A (BA), RGB37.3B (BA), RGB38.4 (BC), RGB38.4A (BC), RGB38.4B (BC)
unnamed: Q2.3 (E2), R3.2, R15.1, U1.4 (IN-)
unnamed: Q2.2 (B1), Q2.4 (B2), U1.1 (OUT)
unnamed: RGB61.6 (GC), RGB61.6A (GC), RGB61.6B (GC), RGB62.1 (GA), RGB62.1A (GA), RGB62.1B (GA)
unnamed: RGB61.5 (RC), RGB61.5A (RC), RGB61.5B (RC), RGB62.2 (RA), RGB62.2A (RA), RGB62.2B (RA)
unnamed: RGB61.4 (BC), RGB61.4A (BC), RGB61.4B (BC), RGB62.3 (BA), RGB62.3A (BA), RGB62.3B (BA)
unnamed: RGB62.6 (GC), RGB62.6A (GC), RGB62.6B (GC), RGB63.1 (GA), RGB63.1A (GA), RGB63.1B (GA)
unnamed: RGB62.5 (RC), RGB62.5A (RC), RGB62.5B (RC), RGB63.2 (RA), RGB63.2A (RA), RGB63.2B (RA)
unnamed: RGB62.4 (BC), RGB62.4A (BC), RGB62.4B (BC), RGB63.3 (BA), RGB63.3A (BA), RGB63.3B (BA)
unnamed: RGB63.6 (GC), RGB63.6A (GC), RGB63.6B (GC), RGB64.1 (GA), RGB64.1A (GA), RGB64.1B (GA)
unnamed: RGB63.5 (RC), RGB63.5A (RC), RGB63.5B (RC), RGB64.2 (RA), RGB64.2A (RA), RGB64.2B (RA)
unnamed: RGB63.4 (BC), RGB63.4A (BC), RGB63.4B (BC), RGB64.3 (BA), RGB64.3A (BA), RGB64.3B (BA)
unnamed: RGB56.1 (GA), RGB56.1A (GA), RGB56.1B (GA), RGB64.6 (GC), RGB64.6A (GC), RGB64.6B (GC)
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

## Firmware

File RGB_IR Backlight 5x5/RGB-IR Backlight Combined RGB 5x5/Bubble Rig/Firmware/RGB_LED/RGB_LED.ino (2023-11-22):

// RGB LED board with individual DAC power quadrant (RGB7x7)
// HHMI Janelia jET SWS 
// 20200728

// processor: Teensy 3.2
// Arduinio IDE: 1.8.310
// 

//  PULSE  a,b,c,d,e, f, C
//    a - pulse width
//    b - pulse period
//    c - # pulses
//    d - off time
//    e - wait time
//    f - number of iterations; 0 = continuous
//    C - color channel ('R', 'G', and/or 'B')
 
//#define DEBUG
#define SYNC_PIN_OUT    // if defined, then SYNC pin is set up as camera trigger out,else it is a trigger in
 
// VERSIONS
//
#define VERSION 20210226

// 20210226 sws
// - extend gain to do all colors (now command is "GAIN color quad value"
 
// 20210223 sws
// - add IRgain for gain control of IR to even out IR backlight if needed

// 20210221 sws
// - add getdacs command to see settings for each quadrant

// 20210214 sws 
// - add watchdog timer; needs modified version of Peter Polidoro's watchdog code to get 'triggered'

// 20210212 sws
// - enables 5-8 were set LOW initially - must be HIGH
// - add pin setup for doutPin

// 20210129 sws
// - add digital board control. 
//    Use pin23 to identify board type (floating is LED, grounded is digital)
//    Use pin22 for chip select of IO expander

// 20210127 sws
// - use analogWrite for markers to allow varying intensity, default to constant on, MARKER cmd to change
//    display current Marker Intensity with MARKER cmd

// 20210117 sws
// - for all on and all off, call ledsOn (Off) with '0' not '0x0f'. The ledsOn(Off) then has the value
//    to turn them all on or off (was 0x0f, now 0xff for 8 'quadrant' setup).
// - don't enable serial2. hasn't been used, and want it for enable 7

// 20201213 sws
// - adding in new form of addOneStep for just duration

// 20201205 sws
// - for colorsSet, check that DAC valeu is less than 0x800 (max allowed) so we can use higher values for 
//      shock and.or aux ouputs
// - save DAC value of 1 for TTL out for shock, so promote a '1' intensity value to '2'

// 20201126 sws
// - add DAC command to set an individual DAC output for testing

// 202011223 sws
// - only send intensity values for quads 1-4 to downstream panels
// - save intensityPC not as percent but as dacvalue and move from newIntensity to setIntensity so
//      that downstream panels save it
// NOTE!!! - we can set intensities for each quadrant, but we only save the last one set (per color)
//   that may cause trouble...

// 20201109 sws
// - add SYNC_PIN_OUT to make sync pin usable as camera trigger out for original RGB board

// 20201029 sws
// - finalize adding in 4 extra chip selects so panel 1 has eight 'quadrants'

// 20201026 sws
// - uee power down at 0% setting. This required a fair amount of change, as when one goes from some brightness to 0
//    or 0% to some value, as power down is also used for Off. Added colorsAreOn boolean to differentiate off from a 
//    0% setting 

// 20201019 sws
// - force SYNC to start when starting experiment
// - only run channels with an on time with RUN command
// - remove default channel setups
// - 

// 20201018 sws
// - allow a 0 sync rate to stop the trigger out, use begin to update or restart the timer

// 20201017 sws
// - when stopping an experiment, need to force markers off. add to HOLD state

// 20201016 sws
// - fixed problem with LED coming on during second step wait time in experiment 

// 20201014 sws
// - add pattern control in Experiment protocol
// - StopExperiment now turns off LEDS and forces state to HOLD

// 20201012 sws
// - added quadrant 'memory' to allow on/off of a pattern (onQuadrants)

// 20200919 sws
//  - wrong index varaible when ending experiment

// 20200910 sws
// - set pulse_counter to 0 at start of experiment to dorec loading of first timer value

// 20200909 sws
// - add elapsed time to getExperimentStatus

// 20200904 sws
// - remove delay secs,msec just use msecs
// - add LED intensity to getexperimentstatus response
// - reset step index to 0 when experiment is done

// 20200903 sws
// - implemented DELAY in experiment 
// - changed duration to seconds

// 20200832 sws
//  - fixed several errors in running multiple steps

// 20200831 sws
//  - iterations was being used as pulse count in experiments
//  - iterations was not being set in experiments 
//  - when epxeriment is not running, getExperimentStatus returned -1, should be 0 

// 20200827 sws
// - experiment commands basically working
// - addExperimentStep returns number of valid steps 

// 20200826 sws
// - added HELP comamd to list comamnds
// - RGB marker LEDs working


// 20200728 sws
// - from RGB_J007017 VER: 20180703 

#include <Cmd.h>
#include <SPI.h>
#include <Watchdog.h>
#include <EEPROM.h>

IntervalTimer pulseTimer;
IntervalTimer syncTimer;

Watchdog watchdog;
    
#define BLUDAC 1
#define GRNDAC 2
#define REDDAC 4
#define IRDAC  8

#define BLUE 0
#define BLU 0
#define GREEN 1
#define GRN 1
#define RED 2
#define IR 3


#define LED_BOARD 1     // if pin23 is floating (existing LED boards) we get this
#define DIGITAL_BOARD 0  // digital boards nust ground pin 23

char colors[4][5] = {"BLU ","GRN ","RED ","IR  "};  // text to show what color number is
uint8_t color2DAC[] = {BLUDAC, GRNDAC, REDDAC, IRDAC}; // translate color number to DAC bit position

#define MAXIRDAC 4095.0    // IR drive can be 0-2.5V (max DAC range)
#define MAXRGBDAC 2047.0   // RGB drive should only go to 1.25V (1/2 DAC range)
 
// --- PINS
//      B2B_RX   0
//      B2B_TX   1
#define DIRpin   2
#define triggerPin  3
#define redPin   4
#define grnPin   5
#define bluPin   6
#define en5Pin   7
#define en6Pin   8
#define en7Pin   9
#define fanPin  10
#define MOSIpin 11
#define SCLKpin 13
#define OTMPpin 14
#define LLpin   15
#define URpin   16
#define LRpin   17
#define ULpin   18
#define SYNCpin 19
#define LEDpin  20
#define en8Pin  21
#define doutPin 22      // cs for digital board
#define boardTypePin 23


#define SYNC_ACTIVE_LOW  // marker pin is active low 

//--- pulse states---
#define OFFSTATE 0
#define START    1
#define WAIT     2
#define PULSEON  3
#define PULSEOFF 4
#define OFFTIME  5
#define CONTINUOUS 6
#define STEPWAIT  7
#define HOLD    8
// ------------------

char states[10][5] = {"off ","strt", "wait","pon ","poff","offt","cont","step","hold"};

#define MINWIDTH     1   //5
#define MAXWIDTH  1800000  //  30 minutes 120000 //30000  //1000  //500
#define MINPERIOD    1   //25
#define MAXPERIOD 1800000  //  30 minutes 120000 //30000  //1000
#define MINPULSES    1
#define MAXPULSES 1000   //40
#define MINOFF       0
#define MAXOFF   1800000  //  30 minutes  120000 //60000  //30000 // 10000
#define MINWAIT      0
#define MAXWAIT    120
#define MINRATE      1
#define MAXRATE   1000
#define MINITERATIONS  0
#define MAXITERATIONS 30000
#define MINSYNC 1
#define MAXSYNC 60

float syncRate = 30;        

int32_t pulse_on_msec[3];
int32_t pulse_off_msec[3];
int32_t off_time_msec[3];
int32_t pulse_count[3];
int32_t wait_sec[3];
int32_t wait_msec[3];
int32_t wait_cnt[3];
int32_t frame_on_msec[3];
int32_t frame_off_msec[3];
uint16_t iteration_loops[3] = {0,0,0};
uint32_t stepDuration;
uint32_t stepDelay;

uint32_t experimentMsecs;

uint8_t bowls =0;

uint16_t intensityPC[4] = {0,0,0,0};

uint16_t iteration[3];

int xIdx = 0;  // index into experiment table

//elapsedMillis pulse_timer;
int32_t pulse_counter[3];
int pulse_enabled[3];

uint16_t frame_on_cnt[3];
uint16_t frame_off_cnt[3];

volatile int32_t next_timer[3];
volatile int8_t flag[3] = {0,0,0};
volatile int8_t ledon[3] = {0,0,0};
volatile int32_t pulse_timer[3];
volatile int8_t  sync_on[3];

boolean markerState[] = {false, false, false};

uint8_t onQuadrants = 0x00;  // track which quadrants are turned on - default to none; bit pattern

uint8_t onColors[] = {0x00, 0x00, 0x00 };  // which colors are set to 0% - Blue, Green, Red , bit pattern for quadrants (up to 8)

boolean colorsAreOn = false;

int pulse_set[3] = {0,0,0};
int pulse_state[3] = {START, START, START };
int last_state[3] = { HOLD, HOLD, HOLD };
boolean markerPin[3] = { bluPin, grnPin, redPin };

int8_t err = 0;

//volatile uint16_t pattern[3] = { 0, 0 , 0 };
volatile uint16_t pattern =  0;

static uint8_t inited = 0;
static uint8_t thisPanel = 0;
// intensity values for each color [4] by number of quads (was 4 now 8)
uint16_t intensity[4][8] =
    {0, 0, 0, 0, 0, 0, 0, 0, 
     0, 0, 0, 0, 0, 0, 0, 0, 
     0, 0, 0, 0, 0, 0, 0, 0, 
     0, 0, 0, 0, 0, 0, 0, 0 };
uint16_t intensityLON = 0;
uint16_t intensityMON = 0;
uint16_t intensityHON = 0;

uint8_t markerIntensity = 255;

float LEDgain[4][4] = 
{
   1.0, 1.0, 1.0, 1.0,  // blue
   1.0, 1.0, 1.0, 1.0,  // green
   1.0, 1.0, 1.0, 1.0,  // red
   1.0, 1.0, 1.0, 1.0   // IR   
};
int EE_INITED = 64;  // address of init code - 4 * 4 * 4 bytes used for gains

boolean bowlEnabled[4] = {false, false, false, false };

boolean wdtReset = false;
          
SPISettings DAC(2000000, MSBFIRST, SPI_MODE2);  
SPISettings DOUT(1000000, MSBFIRST, SPI_MODE0);

float readFloat(unsigned int addr)
{
  union
 {
   byte b[4];
  float f;
 }  data;
 for(int i = 0; i < 4; i++)
 {
  data.b[i] = EEPROM.read(addr+i);
 }
 return data.f;
}

void writeFloat(unsigned int addr, float x)
{
  union
  {
   byte b[4];
   float f;
  } data;
  data.f = x;
  for(int i = 0; i < 4; i++)
  {
    EEPROM.write(addr+i, data.b[i]);
  }
}
 

// =========== S E R I A L    C O M M A N D S =========

#define SETOFF      0x00
#define SETON       0x40
#define SETCOLOR    0x80
#define INTENSITYLON    0xC0
#define INTENSITYMON    0xD0
#define INTENSITYHON    0xE0
#define ENUMERATE1   0xF1  
#define ENUMERATE2   0xF2  
#define ENUMERATE3   0xF3
#define SERIES      0xF4
#define PARALLEL    0xF5
#define COLORSET    0xF8

#define PANELBITS  0x30
#define COLORBITS  0x03
#define QUADBITS   0x0c

#define ALLPANELS 0x00
#define ALLQUADS  0x0f

// ===========================
// ===  C O L O R   S E T  ===
// ===========================

// Turn on selected colors, turn others off

void colorSet(int8_t colors)
{
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

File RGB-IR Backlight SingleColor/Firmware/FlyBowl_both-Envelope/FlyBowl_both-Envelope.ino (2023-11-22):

// Fly Bowl Board Code
// 20140521 sws ID&F Janelia, HHMI
// based on Olfactory arena code
// Target: Teensy 2.0 controller
// Built with: Arduino 1.6.4 with Teensy extensions


// CHR pc  - set chrimson brightness
// IR pc – set IR brightness
// ON x,y  - turn on Chr LEDs
// OFF x,y – turn off Chr LEDs/
//
// Where:
// -	 pc is percent of full brightness (0-100). A 0 value will be off
// -	x is the column of the area to turn on, 1-4 , 0 will turn on (or off) all areas in the row set by ‘y’
// -	y is the row to of the area to turn on, 1-4 , 0 will turn on (or off) all areas in the column set by ‘x’.
// -	a 0,0 value for x and y will change all areas
//
// There is no separate on/off for the IR LEDs.

/*
Janelia Open-Source Software (3-clause BSD License)

Copyright 2022 Howard Hughes Medical Institute

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
1. Redistributions of source code must retain the above copyright notice, this
list of conditions and the following disclaimer.

2. Redistributions in binary form must reproduce the above copyright notice,
this list of conditions and the following disclaimer in the documentation and/or
other materials provided with the distribution.

3. Neither the name of the copyright holder nor the names of its contributors
may be used to endorse or promote products derived from this software without
specific prior written permission.

THIS SOFTWARE IS PROVIDED BY THE COPYRIGHT HOLDERS AND CONTRIBUTORS "AS IS" AND
ANY EXPRESS OR IMPLIED WARRANTIES, INCLUDING, BUT NOT LIMITED TO, THE IMPLIED
WARRANTIES OF MERCHANTABILITY AND FITNESS FOR A PARTICULAR PURPOSE ARE
DISCLAIMED. IN NO EVENT SHALL THE COPYRIGHT HOLDER OR CONTRIBUTORS BE LIABLE FOR
ANY DIRECT, INDIRECT, INCIDENTAL, SPECIAL, EXEMPLARY, OR CONSEQUENTIAL DAMAGES
(INCLUDING, BUT NOT LIMITED TO, PROCUREMENT OF SUBSTITUTE GOODS OR SERVICES;
LOSS OF USE, DATA, OR PROFITS; OR BUSINESS INTERRUPTION) HOWEVER CAUSED AND ON
ANY THEORY OF LIABILITY, WHETHER IN CONTRACT, STRICT LIABILITY, OR TORT
(INCLUDING NEGLIGENCE OR OTHERWISE) ARISING IN ANY WAY OUT OF THE USE OF THIS
SOFTWARE, EVEN IF ADVISED OF THE POSSIBILITY OF SUCH DAMAGE.
  
*/

//#define USE_SCALING  // define this to allow log brightness control
#define LINEAR_DRIVER  //define this if linear driver
//#define USE_EXT_TRIG  // enable this to use ext trigger
//#define MARKER_ACTIVE_LOW  // marker pin is active low 

// #define DEBUG // enable to send debug info out serial USB

#define VERSION "20200224ENV"

// 20200224ENV sws
// - force state to HOLD when STOP is sent to be sure marker LED is turned off

// 20170222ENV sws
// - special for Salk Institute - have marker envelope the pulses since short pulses would not be caught at low frame rates

// 20170228 sws
// - add DEBUG define to stop debug info all the time

// 20170209 sws
// - increase on time and period to 300 seconds

//  20170126 sws
//  - add ext trig note on ???

// 20160120 sws
// - add CNT command to enter in Chrimson setting as 0-4095 DAC counts
//    note that most controllers have a 10 bit DAC so only will change every 4th value
//     but a drop-in DAC can be substituted that is 12 bits (0-4095)


// 20160115 sws
// - change intensity to float to utilize DAC resolution better

// 20150615 sws
// - use define to turn ext trig capability on and off
// - set max offtime to 60 secs not 30

// 20150606 sws
// - add in calibartion for Chr
//    "CAL val" or "CAL ON" or "CAL OFF"

// 20150602 sws
// - changes for Tihana
//       - set setting to 0xffff in setup
//       -  change ext trig to turn LEDs on with high level 

// 20150218 sws
// - lengthen max pulse width and period from 1000 to 30000 msecs
// - change STOP to PAUSE and make STOP reset the timer

// 20150120 sws
// - at RUN with no wait time, the timer would wait out whatever remaining counts
//    there were from the previous run; add line to force counrt to 0 at run with no wait
// - add LIN and LOG commands to set scaling - default to LIN (linear)
// - add iterations to pulse mode to set number of loops of pulses

// 20141206 sws
// - move setup info from setup to ??? cmd

// 20141116 sws
// - Skip any non-printable chars at end of input line; CR after LF was messing things up

//20141026
// - Marker LED setting is opposite for Linear vs Switched code

//20141025 sws
// - add IR enable pin

//20141023 sws
// - EXT command with READY and DONE ouputs
// - turn off LEDS when STOP cmd is sent

// 20140927 sws
// - print out mode at start up
// - fine tune offset on non-linear to allow lowest brightness (may not light all LEDS at lowest settings)

// 20140923 sws
// combine all flavors into one - use the defines above to set proper behavior

// 20140923 sws
// allow disabling of scaling (USE_SCALING)

// 20140917 sws
// turn off print pulse state

// 20140914 sws
//  - add PATT command and use setting to hold pattern
//      modify the pulse interrupt to use pattern
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

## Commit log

2023-11-22 Update README.md
    Add in description of the boards.
2024-04-17 Correct 5x5 RGB BOM errors and add PCB spec
    Added PCB specs to 5x5 RGB
    Corrected BOM errors on 5x5 RGB
    [RGB_IR_J010131revC.xlsx]
2024-05-08 Added PCB files
    [7inLED-cntr-J010130C.brd, 7inLED-cntr-J010130C.sch, 7x7RGB-IR-J010129A.brd, 7x7RGB-IR-J010129A.sch]
2024-05-21 Add 7x7 RGB files
    Add current PCB and cable assembly files for 7x7 RGB panel
    [7inLED-cntr-J010130C.xlsx, 7x7RGB-IR-J010129B.brd, 7x7RGB-IR-J010129B.sch, 7x7RGB-IR-J010129B.xlsx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]
2024-05-21 Updated board files
    New Board files for 7x7 RGB, including manufacturing specs for aluminum substrate
2024-06-24 board change and FW update
    Change Teensy connector to two parts so it can be put into Circuithub
    Fix markerCmd - digital changes weren't changing pin state
    [7inLED-cntr-J010130C.brd, 7inLED-cntr-J010130C.sch]
2024-10-15 FW update and Board correction
    P4 should be a SM shrouded male header, not through hole
    [7x7RGB-IR-J010129B.xlsx]
2025-01-11 Update BOM and firmware
    Comment out DEBUG define in FW
    Update costing in BOM
    Correct quantities, etc in BOM
    [7inLED-cntr-J010130C.brd, 7inLED-cntr-J010130C.sch, 7inLED-cntr-J010130C.xlsx, RGB_IR_J010131revC.brd]
2025-01-31 add enumerate cmd, turn on default layers in PCB
2025-07-14 Add LED data sheet and diffuser
    [Diffuser5x5.dxf]
2025-07-31 fix error in calibration documentation
2025-08-11 update doc to current MARKER cmd, and in FW, don't add offset and gain to a zero DAC value
2025-09-16 board cleanup, doc cleanup, disable DEBUG in code
    [RGB_IR_J010131revC.brd]
2025-10-22 heatsinks, minor code change
2026-03-25 Add Marker Board

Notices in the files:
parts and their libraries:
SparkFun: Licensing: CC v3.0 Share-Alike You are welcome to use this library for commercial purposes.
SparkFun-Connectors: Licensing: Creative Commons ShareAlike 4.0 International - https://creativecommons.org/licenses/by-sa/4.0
